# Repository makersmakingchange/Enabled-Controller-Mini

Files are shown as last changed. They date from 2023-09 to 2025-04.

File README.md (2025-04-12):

# Enabled-Controller-Mini

Enabled Controller Mini is a more affordable version of <a href="https://github.com/milador/Enabled-Controller">Enabled-Controller</a> which is an open-source switch controller interface that enables those with limited or no hand movement to use Adaptive switches as input to operate and perform joystick actions.

<p align="center">
Enabled Controller Mini
</p>

The device offers up to four switch input enclosures through four 3.5mm audio jacks and two analog inputs through one 3.5mm headphone jack. The one 3.5mm headphone jacks can be used to connect one X-Y analog joystick.

The internal RGB led of QT Py board is used to provide visual feedback for each action.

## Assembly Instructions Manual

The <a href="https://github.com/milador/Enabled-Controller-Mini/blob/main/Documentation/Build_Manuals/Enabled_Controller_Mini_Instructions_Manual.pdf">Assembly Instructions Manual</a> is available to download.

## Parts
The <a href="https://github.com/milador/Enabled-Controller-Mini/blob/main/Components/Enabled_Controller_Mini_BOM.csv">BOM</a> file is available to download.

## Software
The first experimental software is under testing.

## Hardware 

### PCB Design 
The <a href="https://github.com/milador/Enabled-Controller-Mini/tree/main/Hardware/PCB">PCB files</a> including both PCB Eagle design files and generated gerber files are available to download.

### Enclosure
The <a href="https://github.com/milador/Enabled-Controller-Mini/tree/main/Hardware/Enclosure">Enclosure files</a> including both STL and STEP enclosure files are available to download.

## License

### Creative Commons Attribution-NonCommercial-ShareAlike (CC-BY-NC-SA)

Copyright (c) 2021 Milador

A creative commons license that bans commercial use and requires you to release any modified works under this license.

<p align="center">
CC-BY-NC-SA
</p>

<br />This work is licensed under a <a rel="license" href="http://creativecommons.org/licenses/by-nc-sa/3.0/">Creative Commons Attribution-NonCommercial-ShareAlike 3.0 Unported License</a>.

<!-- ABOUT MMC START -->
## About Makers Making Change
[Makers Making Change Logo](https://www.makersmakingchange.com/)

Makers Making Change is a program of [Neil Squire](https://www.neilsquire.ca/), a Canadian non-profit that uses technology, knowledge, and passion to empower people with disabilities.

Makers Making Change leverages the capacity of community based Makers, Disability Professionals and Volunteers to develop and deliver affordable Open Source Assistive Technologies.

 - Website: [www.MakersMakingChange.com](https://www.makersmakingchange.com/)
 - GitHub: [makersmakingchange](https://github.com/makersmakingchange)
 - Bluesky: [@makersmakingchange.bsky.social](https://bsky.app/profile/makersmakingchange.bsky.social)
 - Instagram: [@makersmakingchange](https://www.instagram.com/makersmakingchange)
 - Facebook: [makersmakechange](https://www.facebook.com/makersmakechange)
 - LinkedIn: [Neil Squire Society](https://www.linkedin.com/company/neil-squire-society/)
 - Thingiverse: [makersmakingchange](https://www.thingiverse.com/makersmakingchange/about)
 - Printables: [MakersMakingChange](https://www.printables.com/@MakersMakingChange)

### Contact Us
For technical questions, to get involved, or to share your experience we encourage you to [visit our website](https://www.makersmakingchange.com/) or [contact us](https://www.makersmakingchange.com/s/contact).
<!-- ABOUT MMC END -->

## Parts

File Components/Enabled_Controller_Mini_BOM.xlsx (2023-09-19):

Index | Quantity | Digikey Part Number | Manufacturer Part Number | Description | Price (CAD) | Unit Price (CAD) | Link
1 | 1 | 1528-4600-ND | 4600 | ADAFRUIT QT PY - SAMD21 DEV BOARD | 8.31 | 8.31 | https://www.digikey.ca/en/products/detail/adafruit-industries-llc/4600/13543375
2 | 2 | S7040-ND | PPPC071LFBN-RC | CONN HDR 7POS 0.1 GOLD | 0.84 | 0.84 | https://www.digikey.ca/en/products/detail/sullins-connector-solutions/PPPC071LFBN-RC/810179
3 | 4 | CP1-3535NG-ND | SJ1-3535NG | CONN JACK STEREO 3.5MM R/A | 1.65 | 1.65 | https://www.digikey.ca/product-detail/en/cui-inc/SJ1-3535NG/CP1-3535NG-ND
4 | 1 | CP-43514-ND | SJ-43514 | CONN JACK 4COND 3.5MM | 1.47 | 1.47 | https://www.digikey.ca/en/products/detail/SJ-43514/CP-43514-ND/368146
5 | 1 | 350-3746-ND | 51513030250F | LIGHTPIPE PNL MT DOME 0.250" | 1.63 | 1.63 | https://www.digikey.ca/en/products/detail/dialight/51513030250F/4965201
 |  |  |  |  | Total Price (CAD) | 19.69

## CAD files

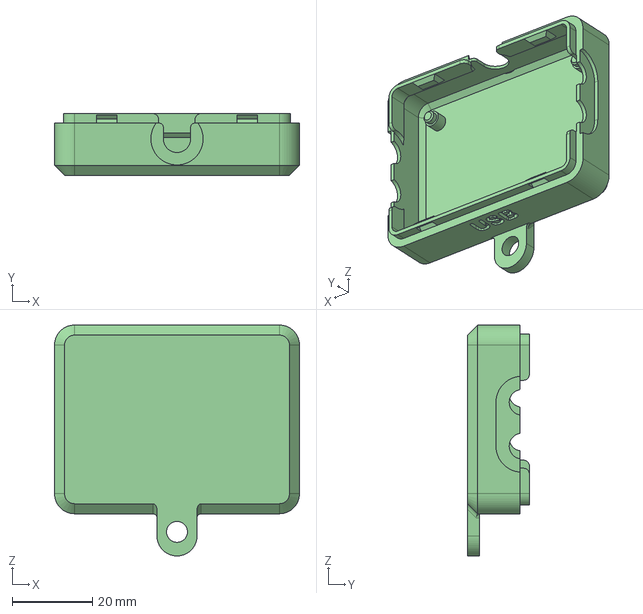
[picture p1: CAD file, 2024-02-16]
Hardware/Enclosure/STEP/Enabled_Controller_Mini_Bottom_With_Mount.step
61.0 x 15.4 x 57.5 mm

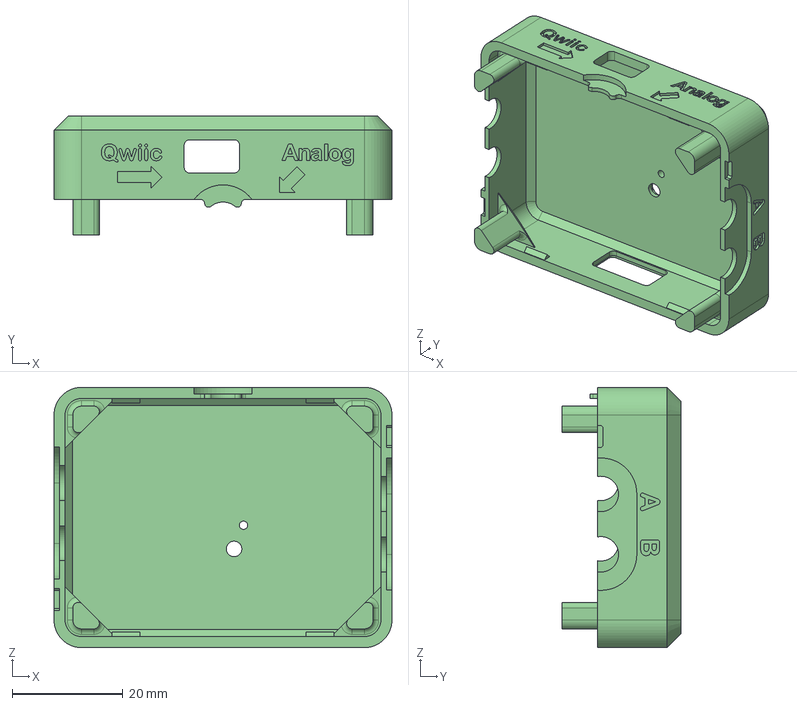
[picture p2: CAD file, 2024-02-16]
Hardware/Enclosure/STEP/Enabled_Controller_Mini_Top.step
61.0 x 21.4 x 47.0 mm

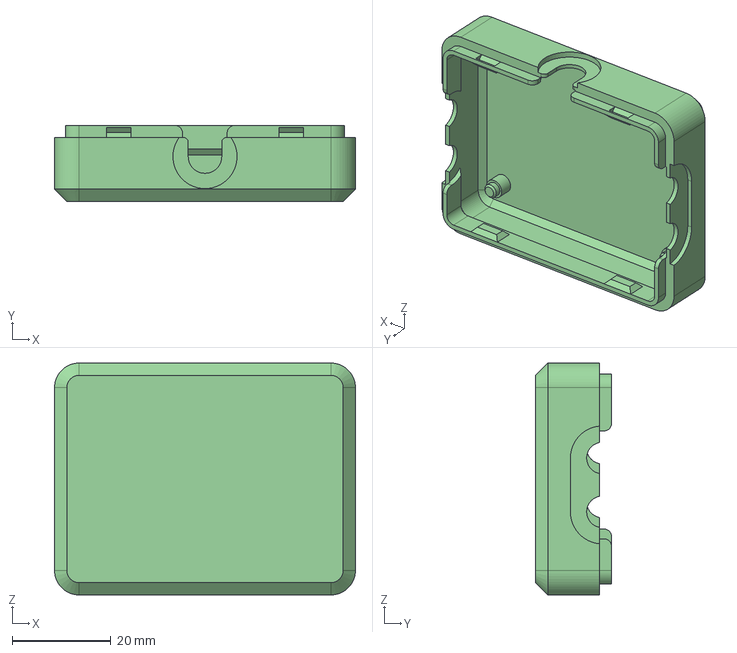
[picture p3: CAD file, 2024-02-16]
Hardware/Enclosure/STEP/Enabled_Controller_Mini_Bottom.step
61.0 x 15.4 x 47.0 mm

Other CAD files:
Hardware/Enclosure/Enabled_Controller_Mini_Bottom.stl
Hardware/Enclosure/Enabled_Controller_Mini_Bottom_With_Mount.stl
Hardware/Enclosure/Enabled_Controller_Mini_Top.stl
Hardware/Enclosure/STL/Enabled_Controller_Mini_Bottom.stl
Hardware/Enclosure/STL/Enabled_Controller_Mini_Bottom_With_Mount.stl
Hardware/Enclosure/STL/Enabled_Controller_Mini_Top.stl

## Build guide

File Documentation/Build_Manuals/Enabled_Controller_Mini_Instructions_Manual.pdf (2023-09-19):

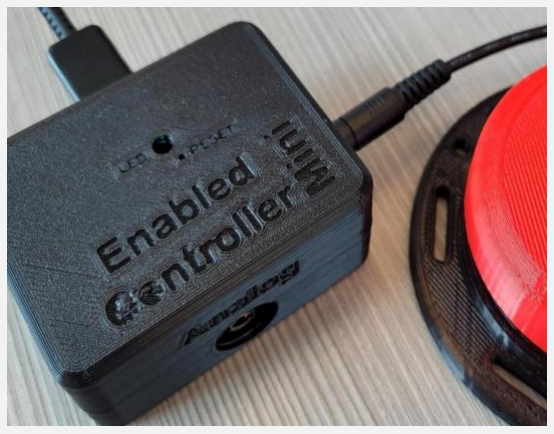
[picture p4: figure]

# ENABLED-CONTROLLER-MINI INSTRUCTIONS MANUAL (V1.3)

An accessible switch adapter box for gaming

### Milad Hajihassan

https://github.com/milador/Enabled-Controller-Mini

1

## Contents

Components List | 2
Software | 3
Installing Arduino IDE | 3
Installing Arduino Libraries | 3
USB Version | 3
Board Support Packages | 3
Required Software and libraries | 4
Uploading Software | 5
Joystick Version | 6
Board Support Packages | 6
Required Software and libraries | 6
Uploading Software | 7
Hardware Assembly | 9
Printed circuit Board design | 9
Enclosure design | 9
Enabled-Controller-Mini Assembly | Error! Bookmark not defined.
Joystick Assembly | 20

2

## Components List

1. ADAFRUIT QT PY - SAMD21 DEV BOARD x 1
2. 7 POSITION HEADER x 2
3. CONN JACK STEREO 3.5MM R/A x 4
4. CONN JACK 4COND 3.5MM x 1
5. LIGHTPIPE PNL MT DOME 0.250" x 1

The bill of materials can also be downloaded from GitHub repository under main directory.

https://github.com/milador/Enabled-Controller-

Mini/blob/master/Components/Enabled_Controller_Mini_BOM.csv (https://github.com/milador/Enabled-Controller-Mini/blob/master/Components/Enabled_Controller_Mini_BOM.csv)

3

## Software

The Enabled-Controller-Mini software can be downloaded from the GitHub repository under software directory.

https://github.com/milador/Enabled-Controller-Mini/tree/master/Software/Arduino/

There are two flavors of Enabled-Controller-Mini and each one requires different hardware. The Enabled-Controller-Mini software is offered in the following flavors:

1. USB Keyboard/Mouse Version
2. Joystick Version

### Installing Arduino IDE

The Arduino IDE is required to compile and upload the source code to the MCU in your Adafruit QT Py board. You can download and install the Arduino from official Arduino website that you can find using following link:

https://www.arduino.cc/en/software

### Installing Arduino Libraries

The following instructions on how to install additional Arduino libraries helps you to get started with setting up Arduino IDE with required libraries and dependencies.

https://www.arduino.cc/en/guide/libraries

### USB Version

Board Support Packages
You can find the official instructions to install Board Support Packages on Adafruit website using following link:

https://learn.adafruit.com/adafruit-qt-py/arduino-ide-setup

Alternatively, you can perform following instructions to install Board Support Packages:

1. Open and start the Arduino IDE.
2. Go to File > Preferences.
3. Add following link as a new line under Additional Board Manager URLs
- https://adafruit.github.io/arduino-board-index/package_adafruit_index.json
4. Restart the Arduino IDE
5. Open the Boards Manager option from the Tools > Board menu and install Adafruit SAMD Boards by Adafruit
6. Wait until the IDE finishes installing the cross-compiling toolchain and tools associated with Board Support Package. This may take few minutes.
7. That’s it! The installation of Board Support Packages is finished.

4

Required Software and libraries
The USB version of the software requires the following files and libraries:
- StopWatch library (https://github.com/RobTillaart/Stopwatch_RT)
- EasyMorse library (https://github.com/milador/EasyMorse)
- Adafruit_NeoPixel library (https://github.com/adafruit/Adafruit_NeoPixel)
- FlashStorage library (https://github.com/cmaglie/FlashStorage)
- Enabled_Controller_Mini_USB_Software.ino (https://raw.githubusercontent.com/milador/Enabled-Controller-Mini/main/Software/Arduino/Enabled_Controller_Mini_USB_Software/Enabled_Controller_Mini_USB_Softw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)

StopWatch library helps to calculate the reaction time and timeout in the morse code interface.

Enabled-Controller-Mini is using Adafruit_NeoPixel library to provide visual feedback using RGB LED.

You can use the following instructions to download and install the required libraries:

1) Visit the StopWatch library (https://github.com/RobTillaart/Stopwatch_RT) github repository page.
2) Click on Code > Download Zip to download StopWatch library.
3) Extract Stopwatch_RT-master.zip file
4) Rename Stopwatch_RT-master folder to Stopwatch folder under Stopwatch_RT-master subdirectory.
5) Copy or move Stopwatch folder to Arduino installation library subdirectory. As an example: This is found under C:\Program Files (x86)\Arduino\libraries in windows 10.
6) Visit the EasyMorse library (https://github.com/milador/EasyMorse) github repository page.
7) Click on Code > Download Zip to download EasyMorse library.
8) Extract EasyMorse-master.zip file
9) Rename EasyMorse-master folder to EasyMorse folder under EasyMorse-master subdirectory.
10) Copy or move EasyMorse folder to Arduino installation library subdirectory. As an example: This is found under C:\Program Files (x86)\Arduino\libraries in windows 10.
11) Visit the FlashStorage library (https://github.com/cmaglie/FlashStorage) github repository page.
12) Click on Code > Download Zip to download FlashStorage library.
13) Extract FlashStorage-master.zip file
14) Rename FlashStorage-master folder to FlashStorage folder under FlashStorage-master subdirectory.
15) Copy or move FlashStorage folder to Arduino installation library subdirectory. As an example: This is found under C:\Program Files (x86)\Arduino\libraries in windows 10.
16) Visit the Enabled_Controller_Mini_USB_Software.ino (https://raw.githubusercontent.com/milador/Enabled-Controller-Mini/main/Software/Arduino/Enabled_Controller_Mini_USB_Software/Enabled_Controller_Mini_USB_Softw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) raw source code file under Enabled-Controller-Mini github repository page.
17) Right click on the source code or any place on this page and select Save Page As…
18) Select the directory you would like to save the software in your computer.
19) Change File name from Enabled_Controller_Mini_USB_Software to Enabled_Controller_Mini_USB_Software.ino
20) Change Save as type to All Files.
21) Click on Save button.
22) Open the directory you selected in step 18.
23) Double left click or open Enabled_Controller_Mini_USB_Software file

5

24) Arduino IDE will ask your permission to create a new sketch folder named Enabled_Controller_Mini_USB_Software and move Enabled_Controller_Mini_USB_Software.ino under this folder.
25) Click on the Ok button.
26) Arduino IDE should now open the Enabled_Controller_Mini_USB_Software.ino file automatically.

Uploading Software
Note: Make sure all files are included in your local copy of Software directory before uploading it to the Adafruit QT PY board. The libraries can be installed in Arduino libraries.

You can go ahead and upload the downloaded .ino code to Adafruit QT PY board using Arduino IDE once all the necessary libraries are installed.

1. Start the Arduino IDE
2. Open Enabled_Controller_Mini_USB_Software.ino
3. Select the Board under Tools > Board > Adafruit SAMD Boards as Adafruit QT PY (SAMD21)
4. Select the correct port number under Tools > Port which should show COM XX (Adafruit QT PY)

Note: It’s very important to make sure the correct Board and port number are selected as selecting the wrong board may result problems with bootloader of Adafruit QT PY board.

5. Press the Verify button to make sure there is no problem with the software and libraries.
6. Press Upload button

You can now go ahead and upload the software. Arduino IDE will show you a Done Uploading message indicating the software is uploaded to your Enabled-Controller-Mini.

The LED on the QT PY board blinks two times in teal to indicate the start of initialization process has been started and it will blink again two times in green to indicate end of the initialization process.

You can also open the Serial Monitor in Arduino IDE on 115200 baud-rate to read initialization information about the version of software.

6

### Joystick Version

Board Support Packages
You can find the official instructions to install Board Support Packages on Adafruit website using following link:

https://learn.adafruit.com/adafruit-qt-py/arduino-ide-setup

Alternatively, you can perform following instructions to install Board Support Packages:

1. Open and start the Arduino IDE.
2. Go to File > Preferences.
3. Add following link as a new line under Additional Board Manager URLs
- https://adafruit.github.io/arduino-board-index/package_adafruit_index.json
4. Restart the Arduino IDE
5. Open the Boards Manager option from the Tools > Board menu and install Adafruit SAMD Boards by Adafruit
6. Wait until the IDE finishes installing the cross-compiling toolchain and tools associated with Board Support Package. This may take few minutes.
7. That’s it! The installation of Board Support Packages is finished.

Required Software and libraries
The Joystick version of the software requires the following files and libraries:
- XACGamepad.h header file (https://github.com/milador/Enabled-Controller-Mini/tree/main/Software/Arduino/Enabled_Controller_Mini_Joystick_Software/XACGamepad.h)
- Adafruit_NeoPixel library (https://github.com/adafruit/Adafruit_NeoPixel)
- Enabled_Controller_Mini_Joystick_Software.ino (https://raw.githubusercontent.com/milador/Enabled-Controller-Mini/main/Software/Arduino/Enabled_Controller_Mini_Joystick_Software/Enabled_Controller_Mini_Joys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)

The XACGamepad.h header file (https://github.com/milador/Enabled-Controller-Mini/tree/main/Software/Arduino/Enabled_Controller_Mini_Joystick_Software/XACGamepad.h) is used to turn Enabled Controller Mini into a XAC Compatible joystick USB HID device which can be used for gaming. It uses TinyUSB USB stack instead of Arduino USB stack to create custom Gamepad USB descriptor.

Enabled-Controller-Mini is using Adafruit_NeoPixel library to provide visual feedback using RGB LED.

You can use the following instructions to download and install the required libraries:

1) Visit the Enabled_Controller_Joystick_Software.ino (https://raw.githubusercontent.com/milador/Enabled-Controller-Mini/main/Software/Arduino/Enabled_Controller_Mini_Joystick_Software/Enabled_Controller_Mini_Joys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) raw source code file under Enabled-Controller-Mini github repository page.
2) Right click on the source code or any place on this page and select Save Page As…
3) Select the directory you would like to save the software in your computer.
4) Change File name from Enabled_Controller_Mini_Joystick_Software to Enabled_Controller_Mini_Joystick_Software.ino
5) Change Save as type to All Files.
6) Click on Save button.
7) Visit the XACGamepad.h header file (https://github.com/milador/Enabled-Controller-Mini/tree/main/Software/Arduino/Enabled_Controller_Mini_Joystick_Software/XACGamepad.h) raw source code file under Enabled-Controller-Mini github repository page.
8) Right click on the source code or any place on this page and select Save Page As…

7

9) Select the same directory that you previously saved Enabled_Controller_Mini_Joystick_Software.ino in step 4.
10) Change File name from XACGamepad to XACGamepad.h
11) Change Save as type to All Files.
12) Click on the Save button.
13) Open the directory you selected in step 4.
14) Double left click or open Enabled_Controller_Mini_Joystick_Software file
15) Arduino IDE will ask your permission to create a new sketch folder named Enabled_Controller_Mini_Joystick_Software and move Enabled_Controller_Mini_Joystick_Software.ino under this folder.
16) Click on the Ok button.
17) Arduino IDE should now open the Enabled_Controller_Mini_Joystick_Software.ino file automatically.

Uploading Software
Note: Make sure all files are included in your local copy of Software directory before uploading it to the Adafruit QT PY board. The libraries can be installed in Arduino libraries.

You can go ahead and upload the downloaded .ino code to Adafruit QT Py board using Arduino IDE once all the necessary libraries are installed.

1. Start the Arduino IDE
2. Open Enabled_Controller_Mini_Joystick _Software.ino
3. Select the Board under Tools > Board > Adafruit SAMD Boards as Adafruit QT PY (SAMD21)
4. Select the USB Stack Tools > USB Stack as TinyUSB
5. Select the correct port number under Tools > Port which should show COM XX (Adafruit QT PY)

Note: It’s very important to make sure the correct Board and port number are selected as selecting the wrong board may result problems with bootloader of Adafruit QT PY board.

6. Press the Verify button to make sure there is no problem with the software and libraries.
7. Press Upload button

You can now go ahead and upload the software. Arduino IDE will show you a Done Uploading message indicating the software is uploaded to your Enabled-Controller-Mini.

The LED on the QT PY board blinks two times in teal to indicate the start of initialization process has been started and it will blink again two times in green to indicate end of the initialization process.

You can also open the Serial Monitor in Arduino IDE on 115200 baud-rate to read initialization information about the version of software.

8

## USB Mouse and Gamepad Software

1.1. Download Arduino IDE for your operating system at https://www.arduino.cc/en/software
1.2. Install Arduino IDE
2. Setup Core
2.1. Open Arduino IDE
2.2. Click on File -> Preferences
2.3. Locate the text field that says Additional Boards Manager URLs beside it.
2.4. Copy and paste the following link into the field as a new line: https://adafruit.github.io/arduino-board-index/package_adafruit_index.json
2.5. Click on OK
2.6. Restart the Arduino IDE
2.7. Open the Boards Manager option from the Tools-> Board-> Boards Manager..., search for “Adafruit SAMD” and select “Adafruit SAMD Boards” by Adafruit
3. Install Libraries
3.1. Go to https://github.com/cyborg5/TinyUSB_Mouse_and_Keyboard and go to Code -> Download ZIP
3.2. Click on Sketch -> Include Library -> Add .ZIP Library
3.2.1. Select “TinyUSB_Mouse_and_Keyboard” from your downloads to add into your Arduino/libraries folder
3.3. Go to Tools -> Manage Libraries…, search for “Flash Storage” and install the library “FlashStorage” by Arduino
3.4. Go to Tools -> Manage Libraries…, search for “Adafruit NeoPixel” and install the library “Adafruit NeoPixel” by Arduino
4. Upload the Code to the joystick
4.1. Open OpenAT_Joystick_Mouse_M0_Software_Enabled_Controller_Mini.ino with Open Arduino IDE.
4.2. Edit the value of Line 36: Mouse_Mode_Enabled, to select either Mouse or Gamepad Mode. True for Mouse Mode, False for Gamepad Mode.
4.3. Select Adafruit QT Py M0 (SAMD21) from Tools -> Board -> Adafruit SAMD Boards
4.4. Click on Tools -> USB Stack and select Adafruit TinyUSB
4.5. Connect the joystick using the USB cable to the computer.
4.6. Select the correct port from Tools -> Port menu.
4.7. Verify and upload the code.

9

## Hardware Assembly

### Printed circuit Board design

The printed circuit boards (PCB) can be downloaded from GitHub repository under Hardware directory.

https://github.com/milador/Enabled-Controller-Mini/tree/master/Hardware/PCB

### Enclosure design

The enclosure/housing files in STL format can be downloaded from GitHub repository under Hardware directory.

https://github.com/milador/Enabled-Controller-Mini/tree/master/Hardware/Enclosure

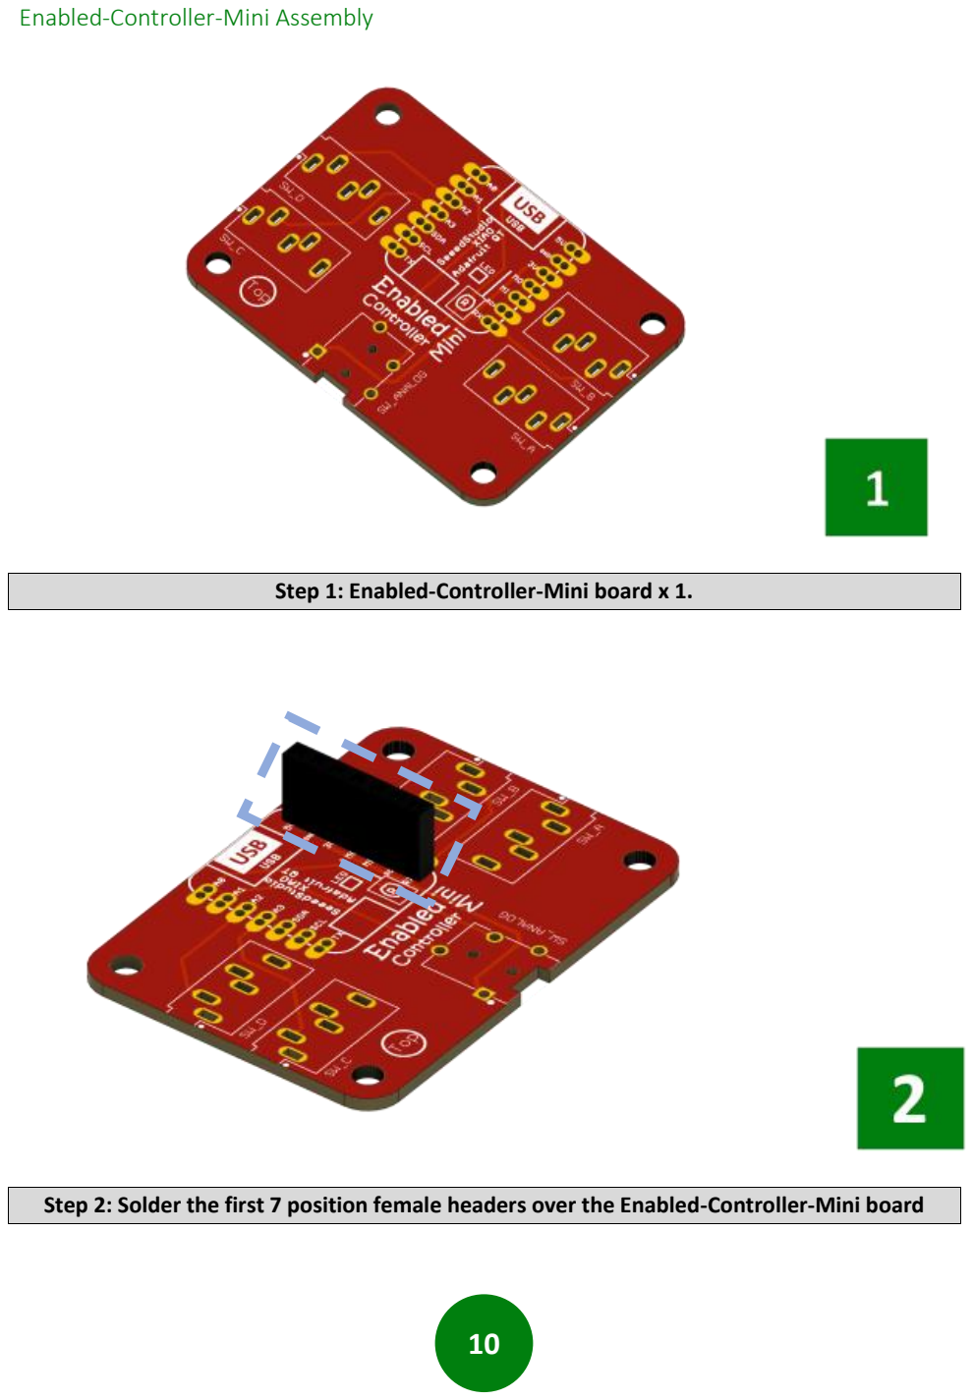
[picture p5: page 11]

10

### Enabled-Controller-Mini Assembly

Step 1: Enabled-Controller-Mini board x 1.
Step 2: Solder the first 7 position female headers over the Enabled-Controller-Mini board

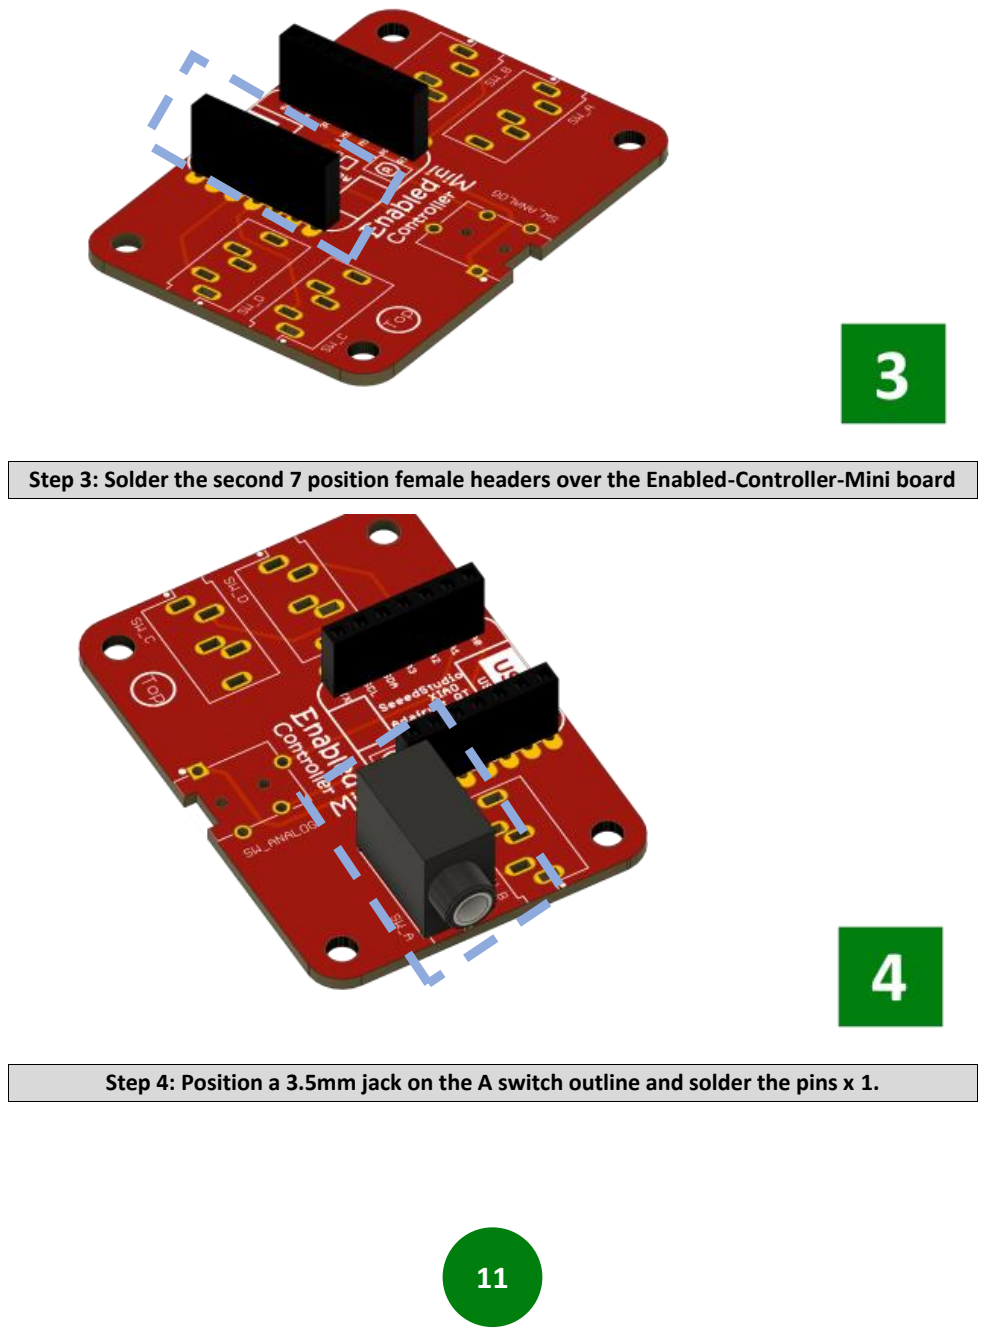
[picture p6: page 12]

11

Step 3: Solder the second 7 position female headers over the Enabled-Controller-Mini board
Step 4: Position a 3.5mm jack on the A switch outline and solder the pins x 1.

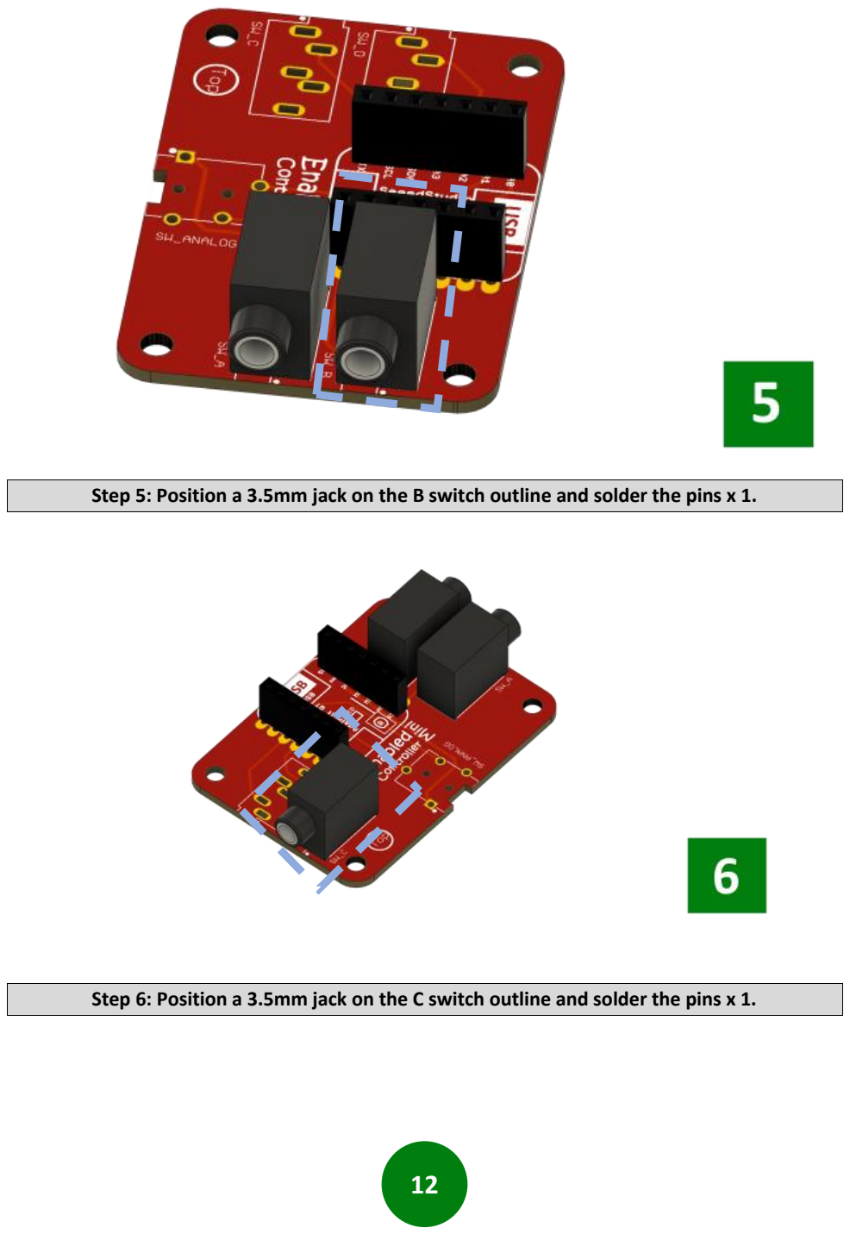
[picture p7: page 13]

12

Step 5: Position a 3.5mm jack on the B switch outline and solder the pins x 1.
Step 6: Position a 3.5mm jack on the C switch outline and solder the pins x 1.

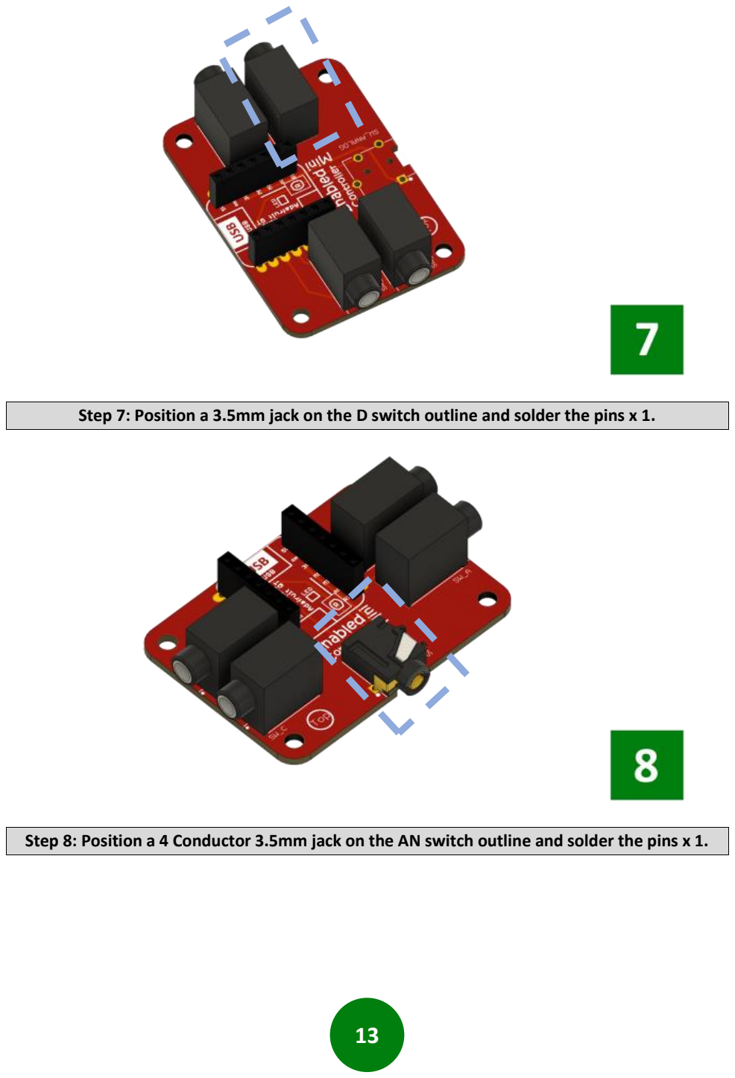
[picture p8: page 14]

13

Step 7: Position a 3.5mm jack on the D switch outline and solder the pins x 1.
Step 8: Position a 4 Conductor 3.5mm jack on the AN switch outline and solder the pins x 1.

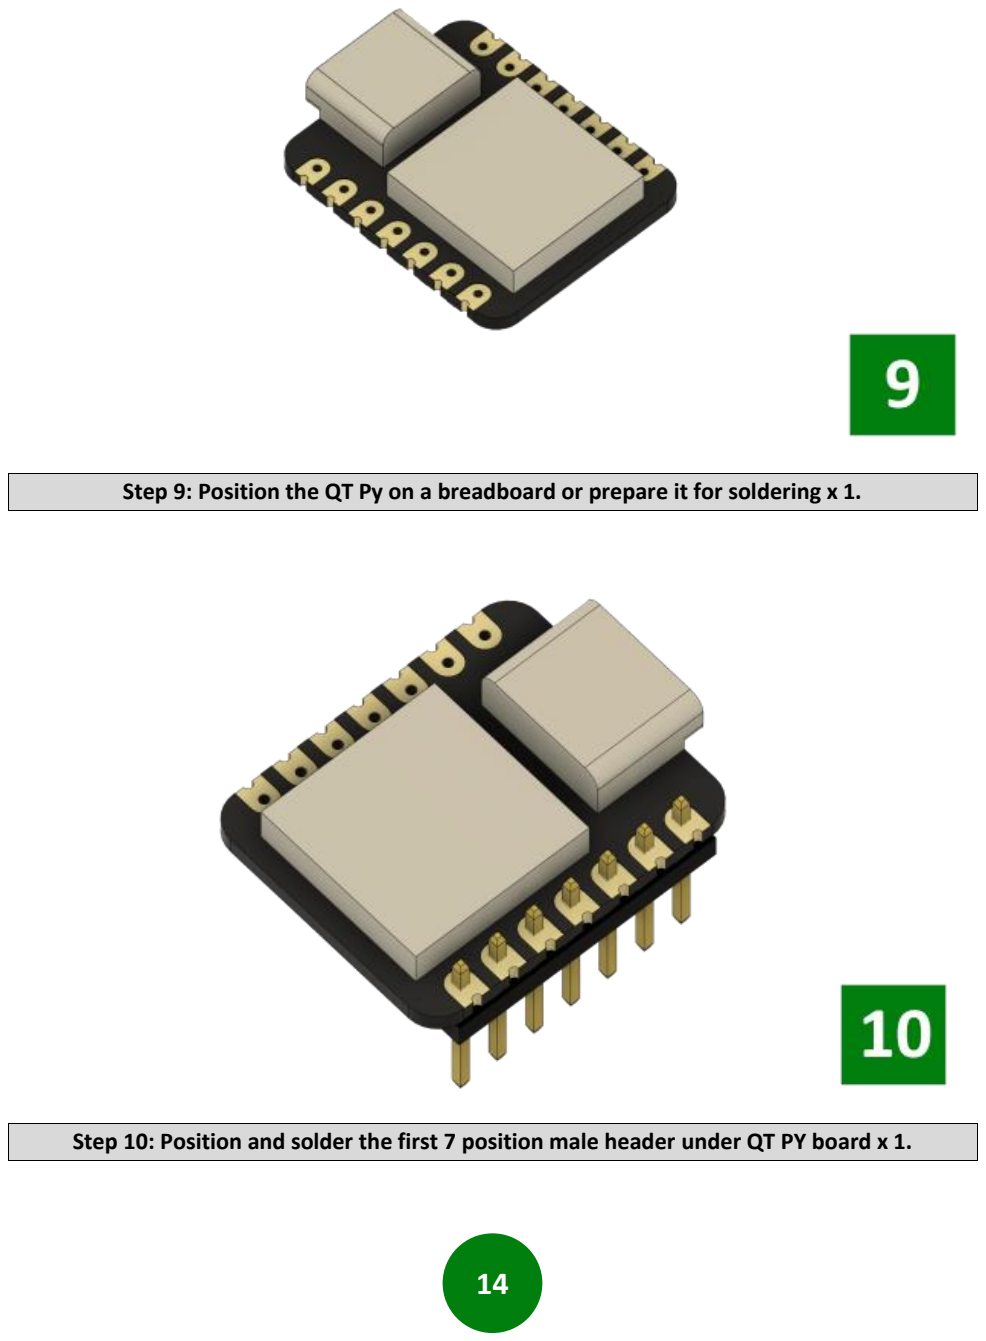
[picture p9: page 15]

14

Step 9: Position the QT Py on a breadboard or prepare it for soldering x 1.
Step 10: Position and solder the first 7 position male header under QT PY board x 1.

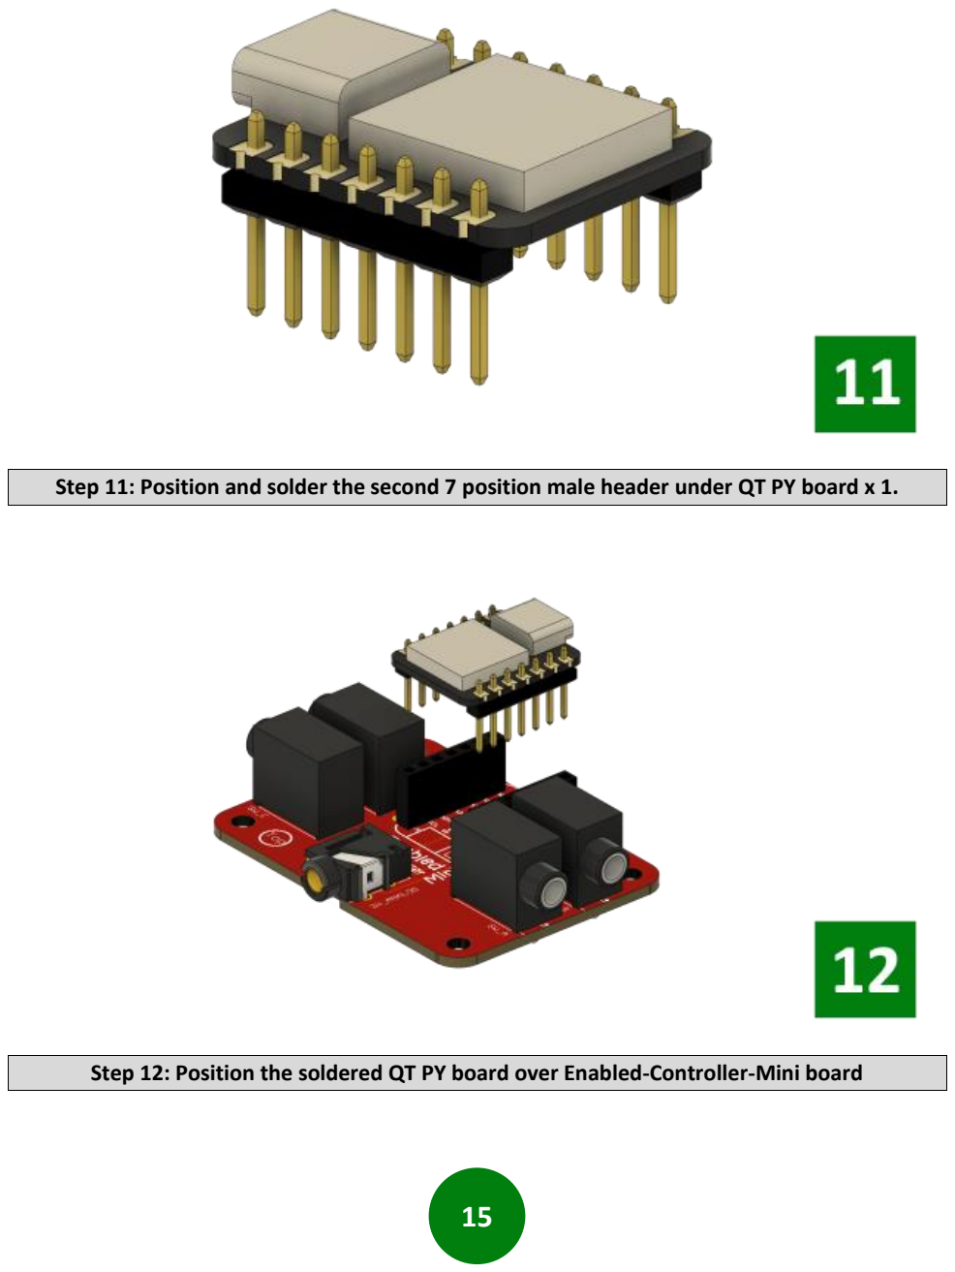
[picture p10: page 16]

15

Step 11: Position and solder the second 7 position male header under QT PY board x 1.
Step 12: Position the soldered QT PY board over Enabled-Controller-Mini board

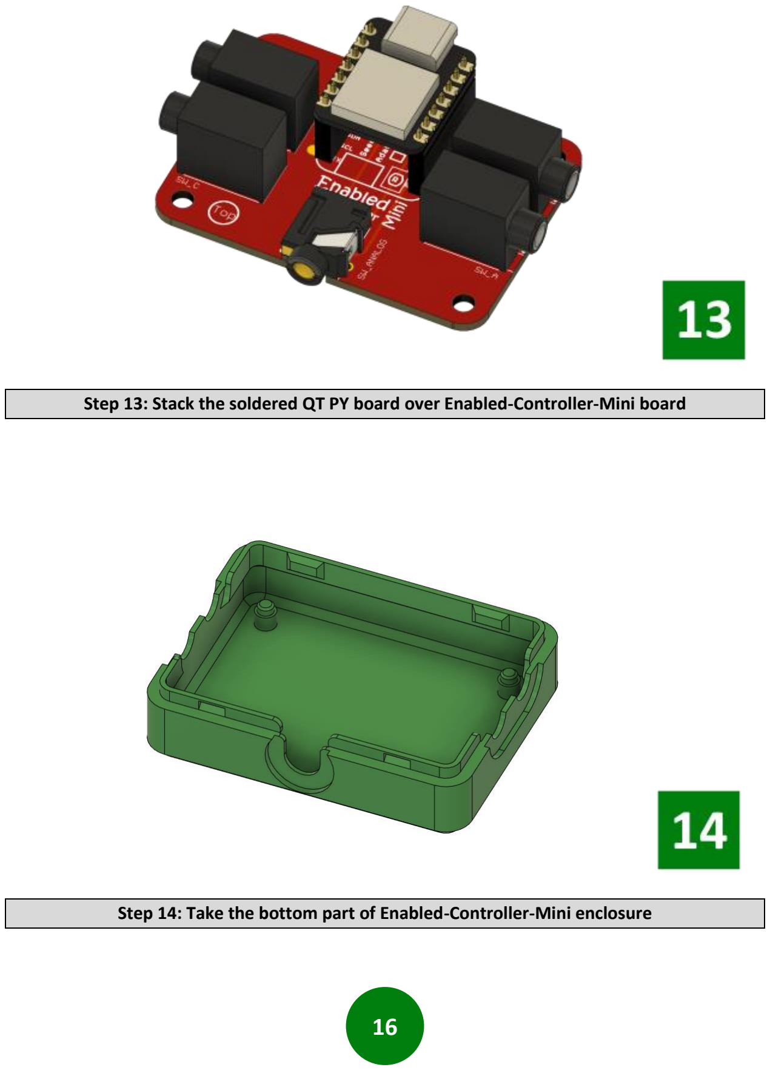
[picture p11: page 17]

16

Step 13: Stack the soldered QT PY board over Enabled-Controller-Mini board
Step 14: Take the bottom part of Enabled-Controller-Mini enclosure

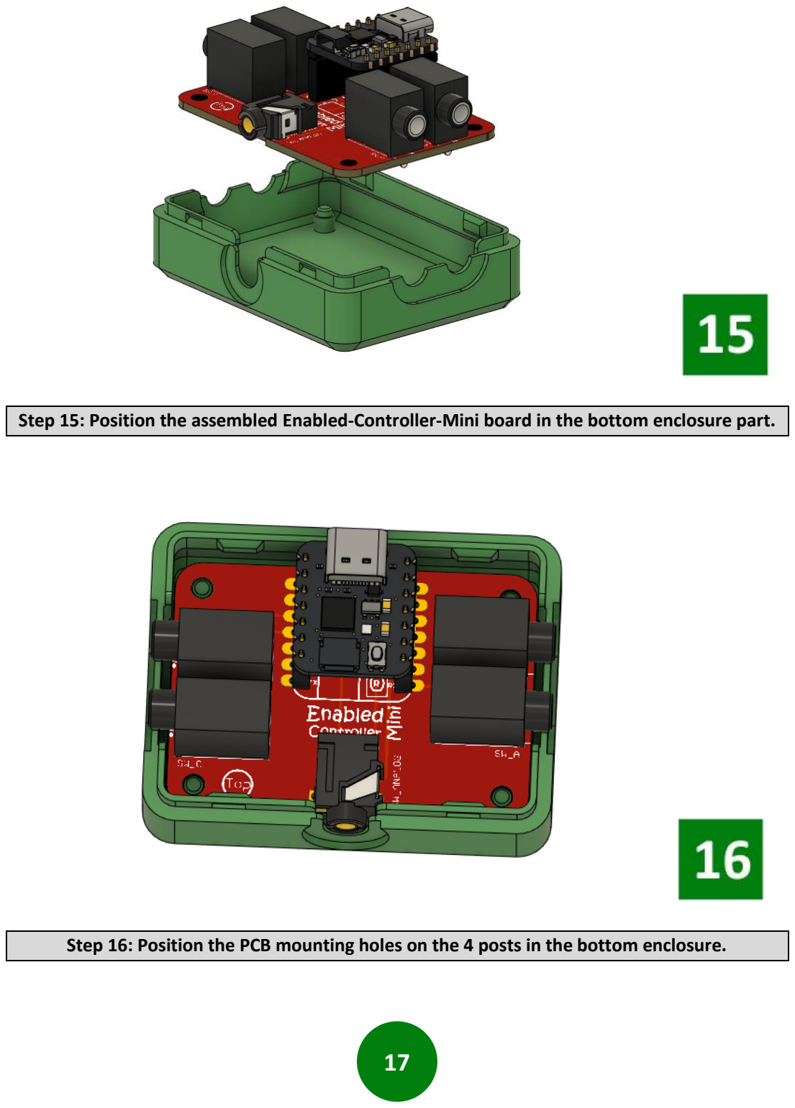
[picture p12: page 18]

17

Step 15: Position the assembled Enabled-Controller-Mini board in the bottom enclosure part.
Step 16: Position the PCB mounting holes on the 4 posts in the bottom enclosure.

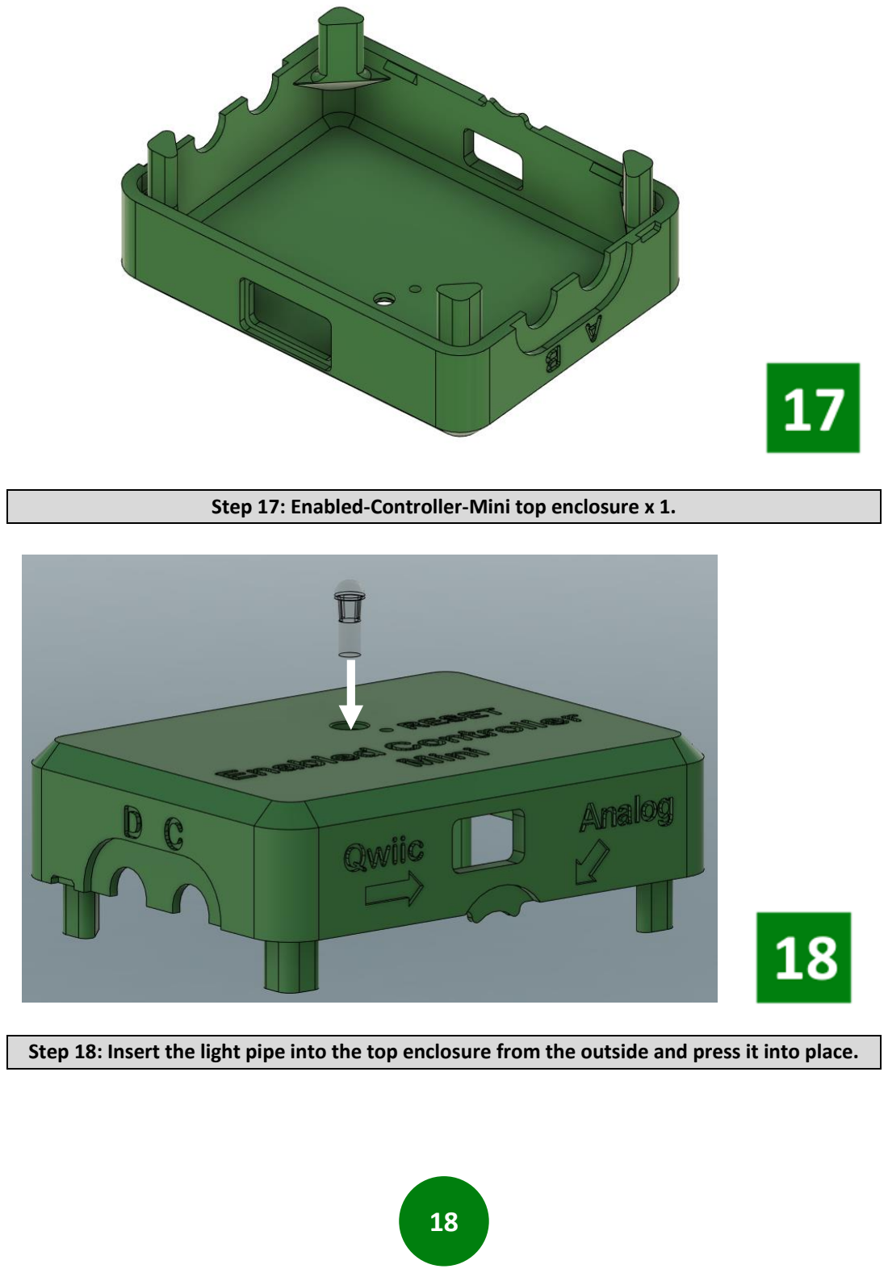
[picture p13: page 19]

18

Step 17: Enabled-Controller-Mini top enclosure x 1.
Step 18: Insert the light pipe into the top enclosure from the outside and press it into place.

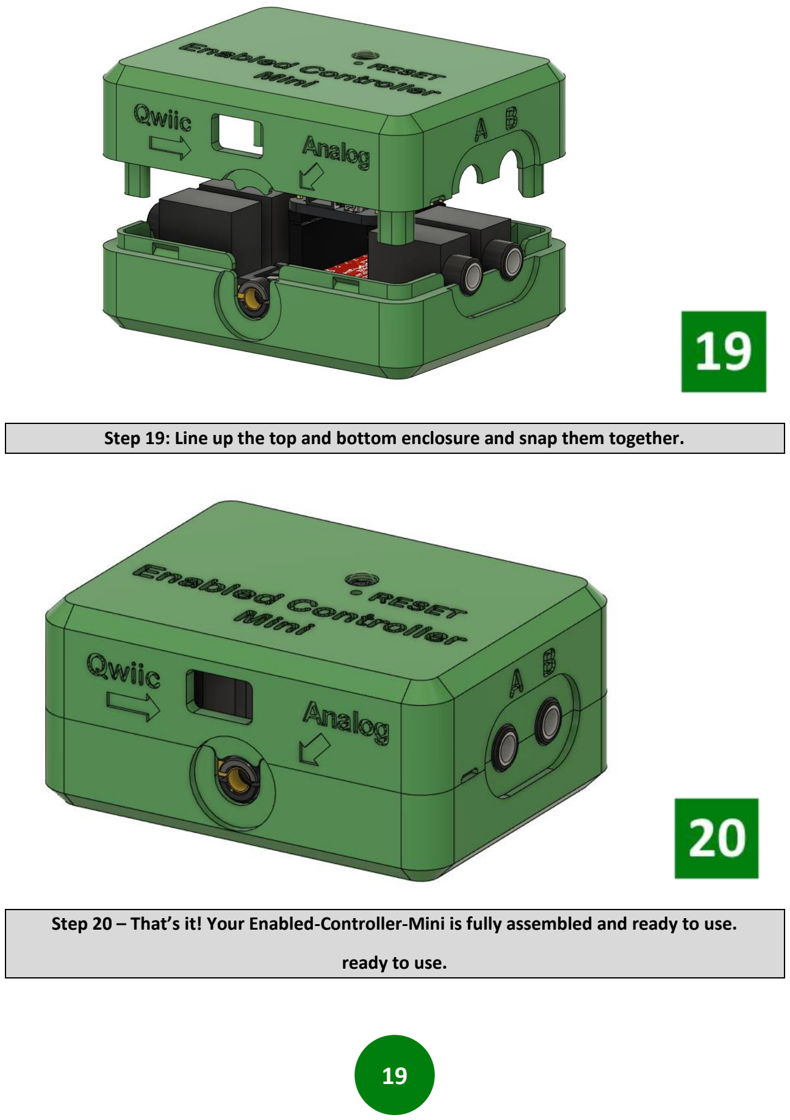
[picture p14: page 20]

19

Step 19: Line up the top and bottom enclosure and snap them together.
Step 20 – That’s it! Your Enabled-Controller-Mini is fully assembled and ready to use.

ready to use.

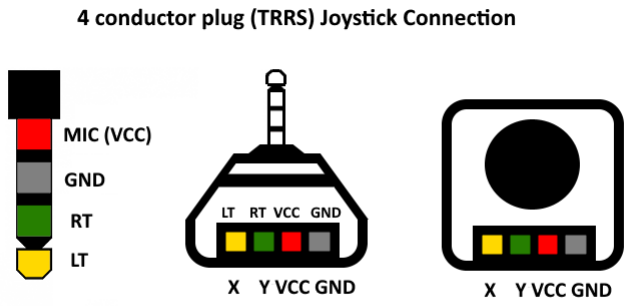
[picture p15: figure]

20

### Joystick Assembly

Enabled-Controller includes one 4 conductors input 3.5mm jack reserved to connect a dual axis joystick. The order of pins in joystick boards can vary depending on the brand but the following general configuration can be used to attach analog joystick. Enabled-Controller is designed to work with analog joystick which rated to work with 3.3V input voltage.

Figure 1: 4 Conductor plug (TRRS) pin mapping

The following table can summarize figure 1 as following:

PIN | FUNCTION
1 (Sleeve) | Microphone – VCC (3.3V)
2 (Ring 2) | GND
3 (Ring 1) | RT(Right Audio Channel)
4 (Tip) | LT(Left Audio Channel)
Table 1: 4 Conductor plug (TRRS) pin mapping

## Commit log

2024-02-16 Add files via upload
    Updated v1.4 STLs
    [Enabled_Controller_Mini_Bottom.stl, Enabled_Controller_Mini_Bottom_With_Mount.stl, Enabled_Controller_Mini_Top.stl]
2024-02-16 Update v1.4 enclosure files
    [Enabled_Controller_Mini_Bottom.step, Enabled_Controller_Mini_Bottom.stl, Enabled_Controller_Mini_Bottom_With_Mount.step, Enabled_Controller_Mini_Bottom_With_Mo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]
